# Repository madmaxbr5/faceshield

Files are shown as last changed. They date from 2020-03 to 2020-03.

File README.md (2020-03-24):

# faceshield
Plans and instructions for a laser-cut face shield for COVID-19 PPE.<br>
<a rel="Latest writeup is here" href="https://docs.google.com/document/d/1kkmi4AXXiO3MM34HUSQM1HEoQGzZ9lCmX02rIgVbk9Q/edit">Latest writeup is here</a>

<a rel= "Changelog" href="https://docs.google.com/spreadsheets/d/1W2J-ytu9fVvlhKfiAqHdhAEgvUPn8Wbc3KxeLBzUL18/edit#gid=0">Current Changlog is here.</a>

The intended material is .005"-.001" (5-10 mil) PET/Mylar/Duralar film or similar, and is available from craft stores or from plastic suppliers. A sourcing document is included in the files. 

Different materials may also be compatible but results are not guaranteed. It is unlikely that this design will be compatible with substrates greater than .015"; modifications will be studied for thicker substrates. 

This work is free to use and modify as needed for non-profit uses. Non-profit for the purpose of this license means revenues not to exceed recovery of material costs, distribution costs, and reasonable rates of manufacturing labor. This is to discourage profiteering or price gouging. Use for profiteering is strictly disallowed. 

<br />This work is licensed under a <a rel="license" href="http://creativecommons.org/licenses/by-sa/4.0/">Creative Commons Attribution-ShareAlike 4.0 International License</a>.

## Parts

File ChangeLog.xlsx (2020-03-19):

Version | Comments | Cut time | Assembly time | 40" Roll yield | Appx Cost per mask
2 | Initial released version | 0:47:00 | 1min | 192 | $0.26
9 | significant update to dimensions and tab structure | 0:45:00 | 2-3min | 225 | $0.22
12 | redesign and simplification of tabs. Tweak to dimensions. Substantial improvement in packing efficiency | 0:38:00 | 10sec | 252 | $0.20

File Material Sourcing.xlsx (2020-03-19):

Supplier | Item | Cost | Link
Grafix/Amazon | 40"x100ft .005 duralar | $98 | https://www.amazon.com/Grafix-Clear-Dura-Lar-40-Inch-100-Feet/dp/B0092MJLSO
Grafix direct | 40"x100ft .005 duralar | $50 (qty 25+) | ken@grafixplastics.com
US plastics | 40"x100ft .005 mylar | $117 | https://www.usplastic.com/catalog/item.aspx?itemid=36640&catid=748
petfilm.com | 1000ft roll .005 PET | TBD | under investigation
blick art | 40"x100ft .005 duralar | $135 | https://www.dickblick.com/items/55506-1509/
tap plastics | .005 mylar various sizes | varied but on the expensive side | https://www.tapplastics.com/product/plastics/plastic_sheets_rolls/mylar_rolls_clear/255

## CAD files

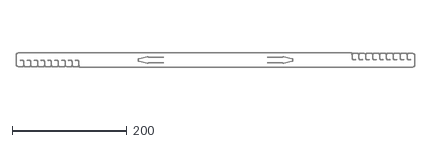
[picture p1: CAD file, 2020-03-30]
Origami_V20_Headband.dxf
694.9 x 25.9

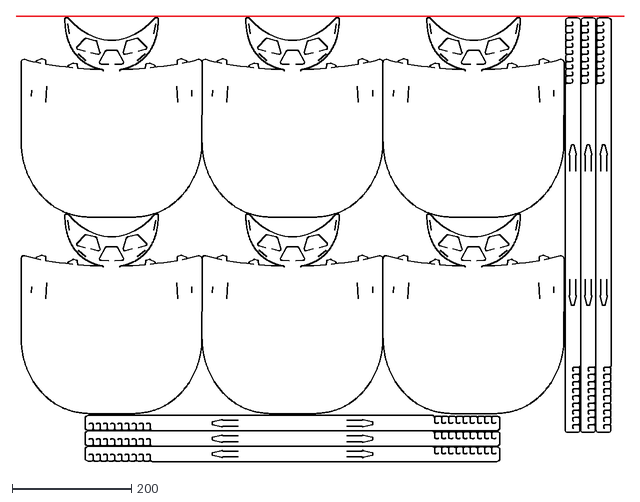
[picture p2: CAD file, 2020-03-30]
Origami_V20_40x30_array.dxf
1018.8 x 746.4

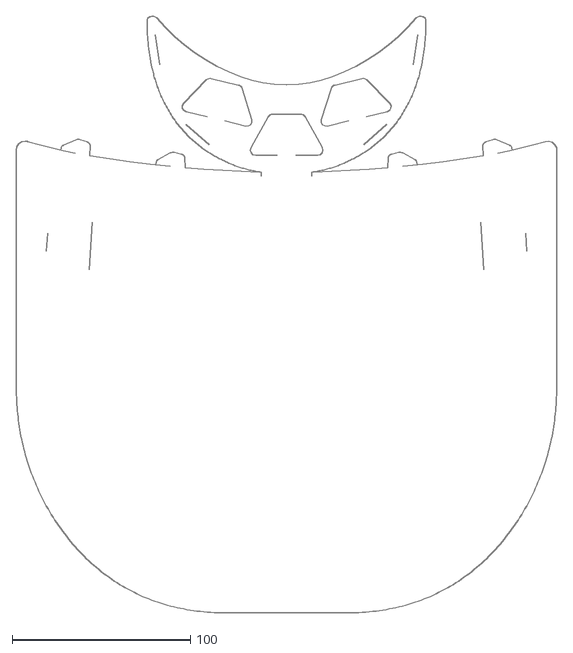
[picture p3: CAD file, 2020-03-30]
Origami_V20_Shield.dxf
303.2 x 334.5

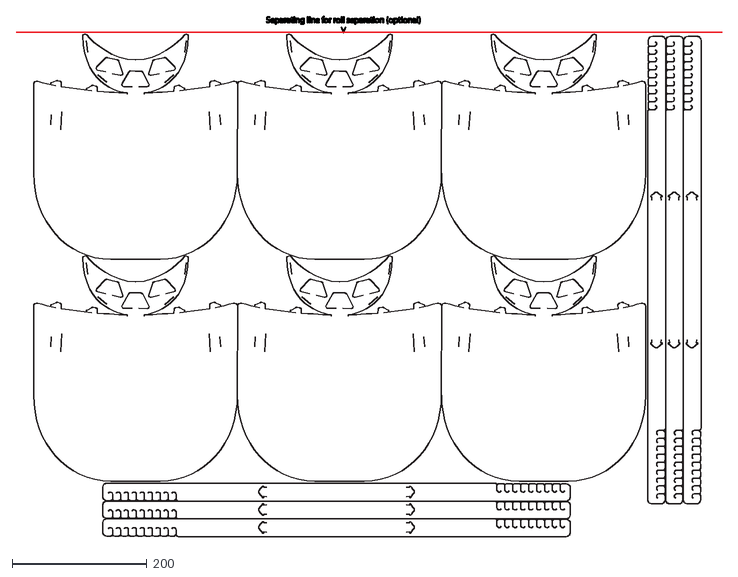
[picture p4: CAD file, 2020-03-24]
origami_face_shield_v16_40x30.dxf
1047.9 x 771.9

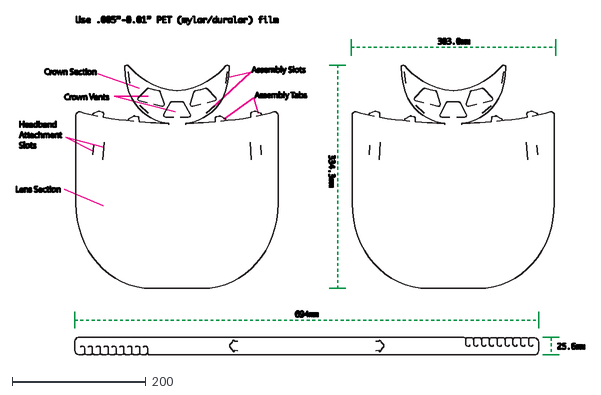
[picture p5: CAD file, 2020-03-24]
origami_face_shield_v16_master.dxf
851.1 x 507.3

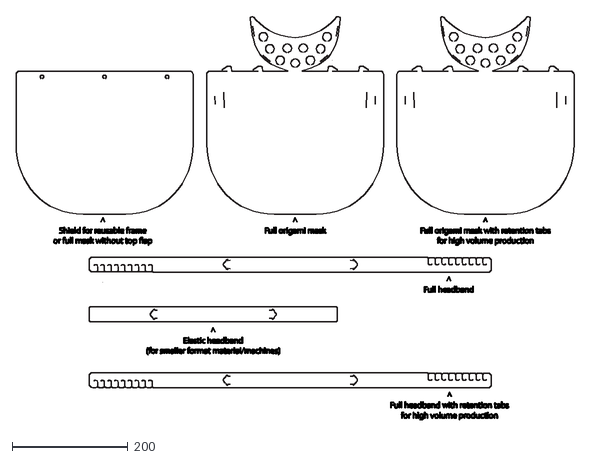
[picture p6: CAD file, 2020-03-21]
shield_laser_template_v15.dxf
962.5 x 696.4

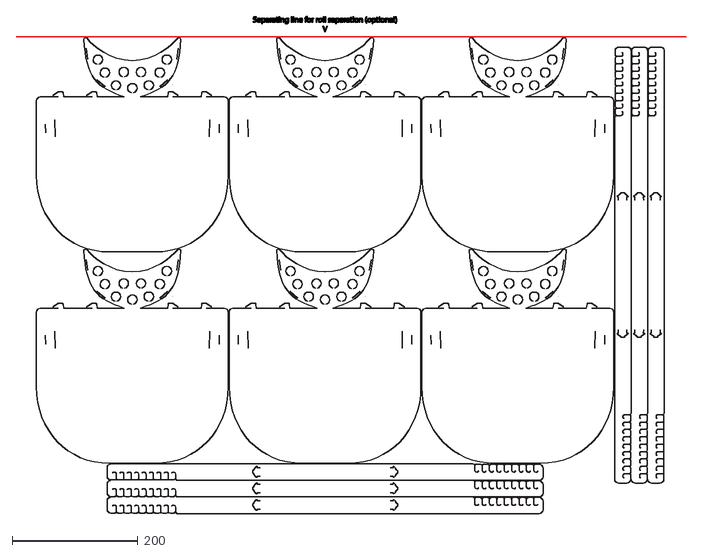
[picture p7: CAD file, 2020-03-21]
shield_laser_template_v15_40inch_roll.dxf
1066.8 x 791.4

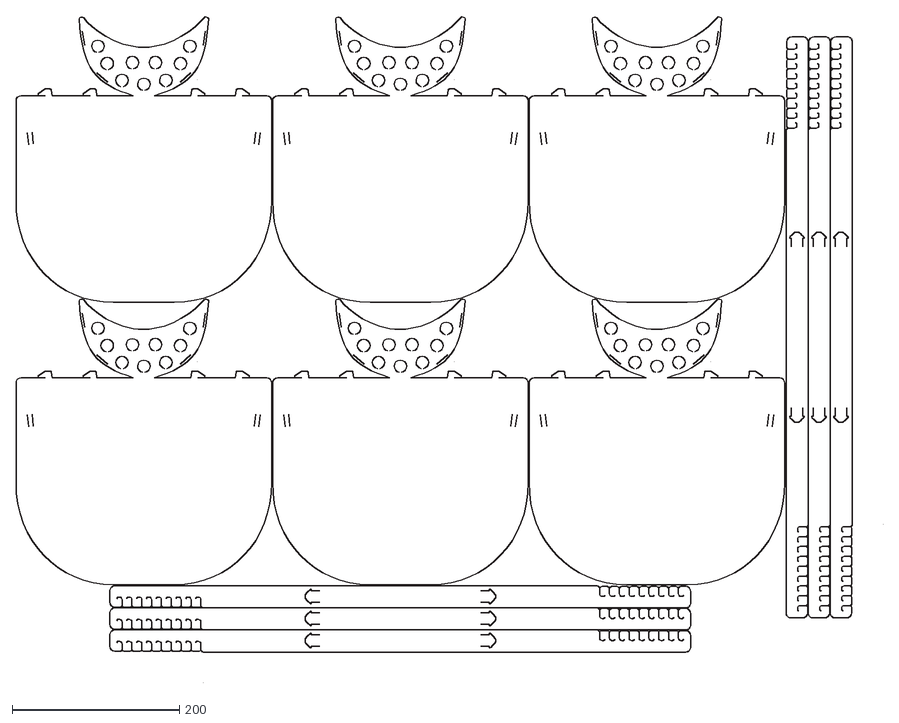
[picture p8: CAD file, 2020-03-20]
shield_laser_template_v14_40inch_roll_revised.dxf
1035.5 x 795.9

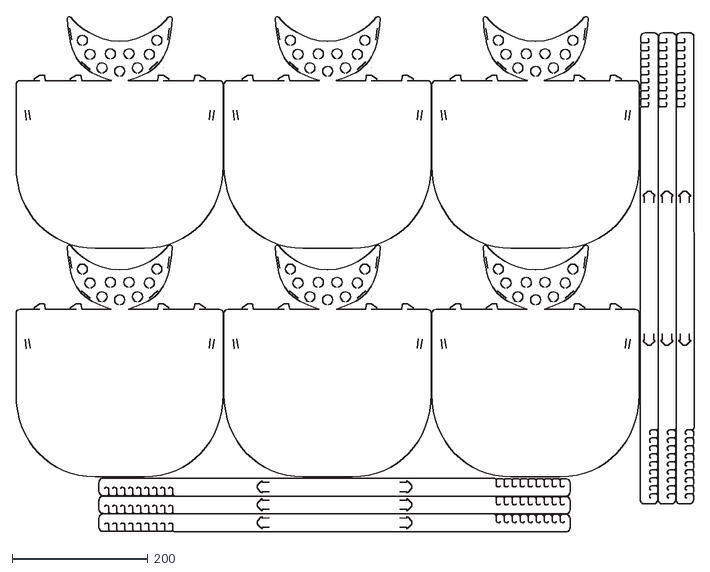
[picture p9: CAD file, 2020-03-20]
shield_laser_template_v14_40inch_roll.dxf
998.9 x 759.8

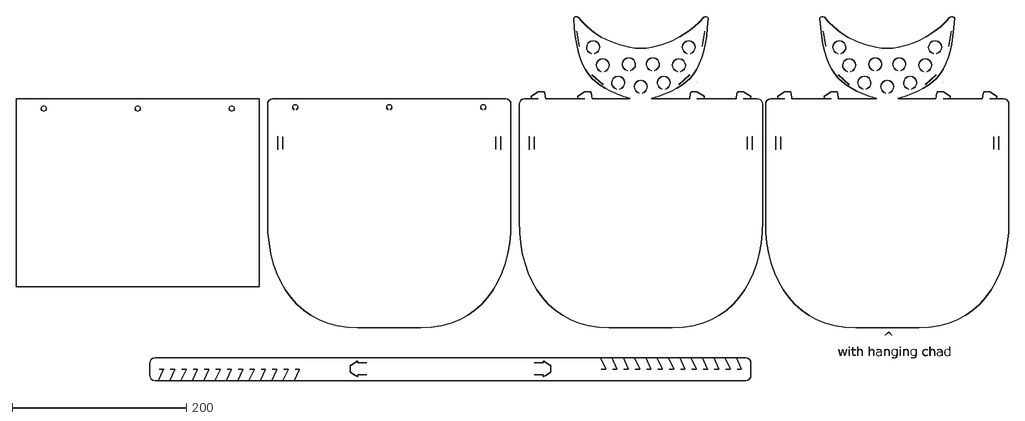
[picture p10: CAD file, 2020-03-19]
shield_laser_template_v12.dxf
^
with hanging chad

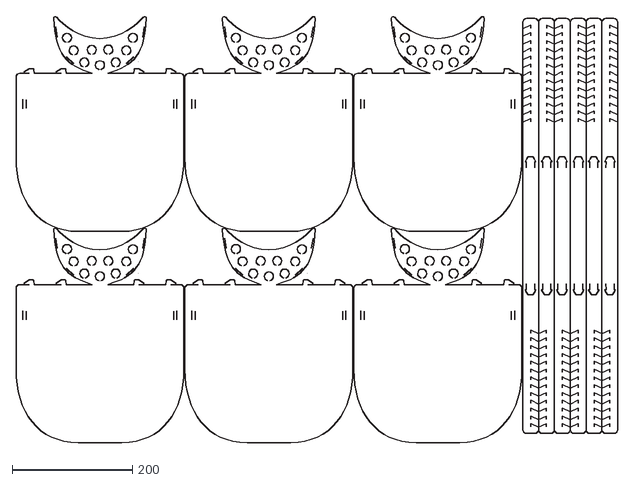
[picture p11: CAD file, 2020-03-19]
shield_laser_template_v12_bulk_40inch_roll.dxf
1001.3 x 709.1

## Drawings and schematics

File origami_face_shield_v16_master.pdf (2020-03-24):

## Use .005”-0.01” PET (mylar/duralar) film

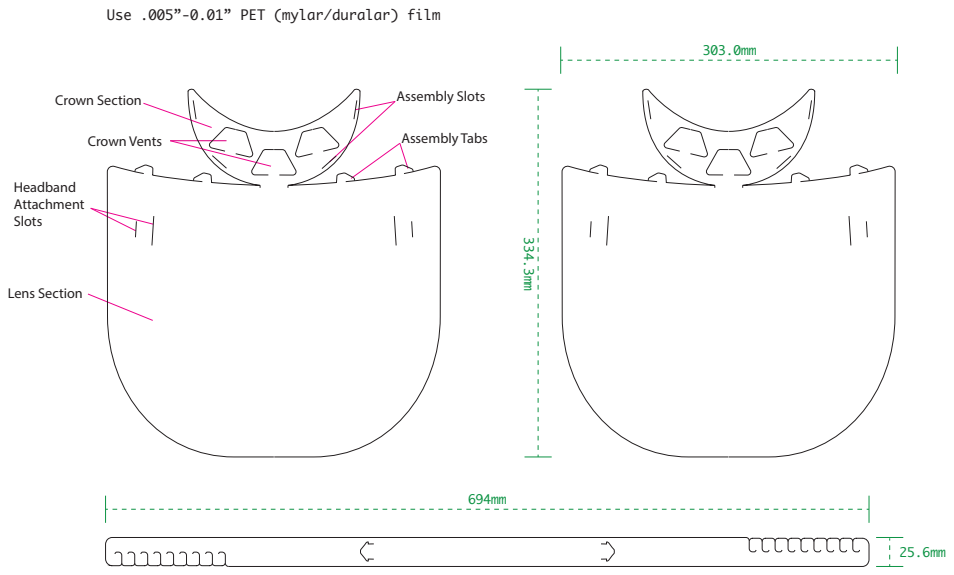
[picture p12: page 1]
Lens Section; Crown Section; Crown Vents; Headband Attachment Slots; Assembly Slots; Assembly Tabs

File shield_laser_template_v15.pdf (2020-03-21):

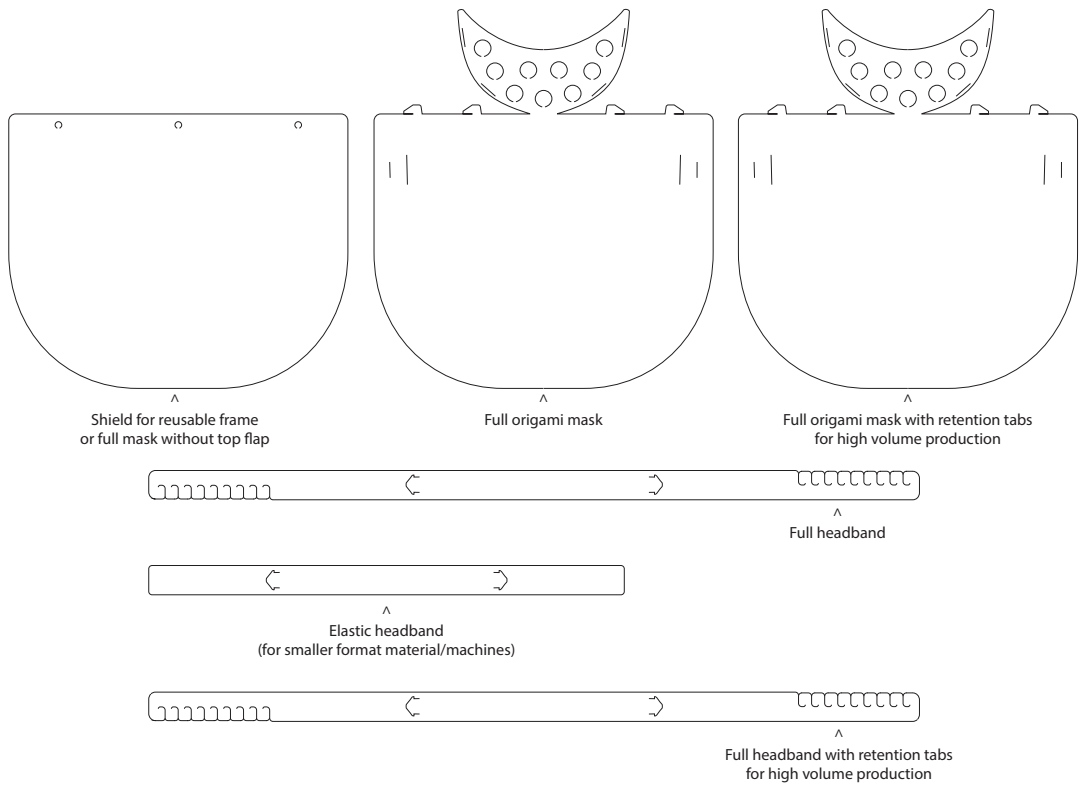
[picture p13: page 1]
^ Full headband; ^ Elastic headband

Full origami mask

Shield for reusable frame
or full mask without top ap

Full origami mask with retention tabs
for high volume production

(for smaller format material/machines)

Full headband with retention tabs

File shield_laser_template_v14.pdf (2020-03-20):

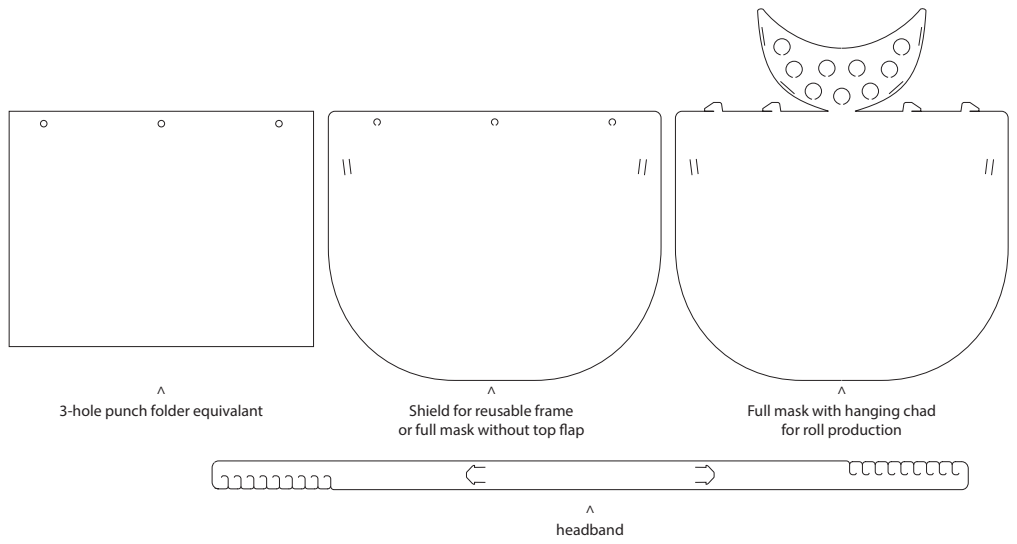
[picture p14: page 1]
^ headband

3-hole punch folder equivalant

Shield for reusable frame
or full mask without top ap

Full mask with hanging chad
for roll production

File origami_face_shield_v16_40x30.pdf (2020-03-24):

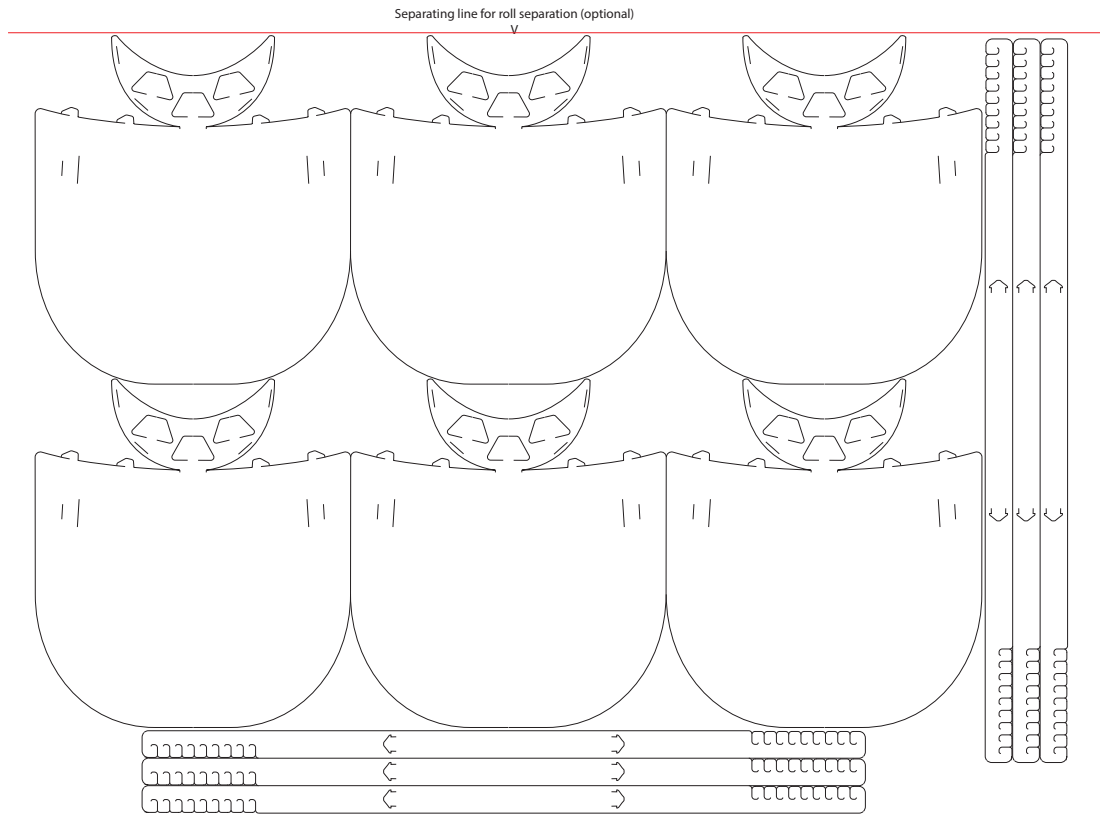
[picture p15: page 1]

Separating line for roll separation (optional)

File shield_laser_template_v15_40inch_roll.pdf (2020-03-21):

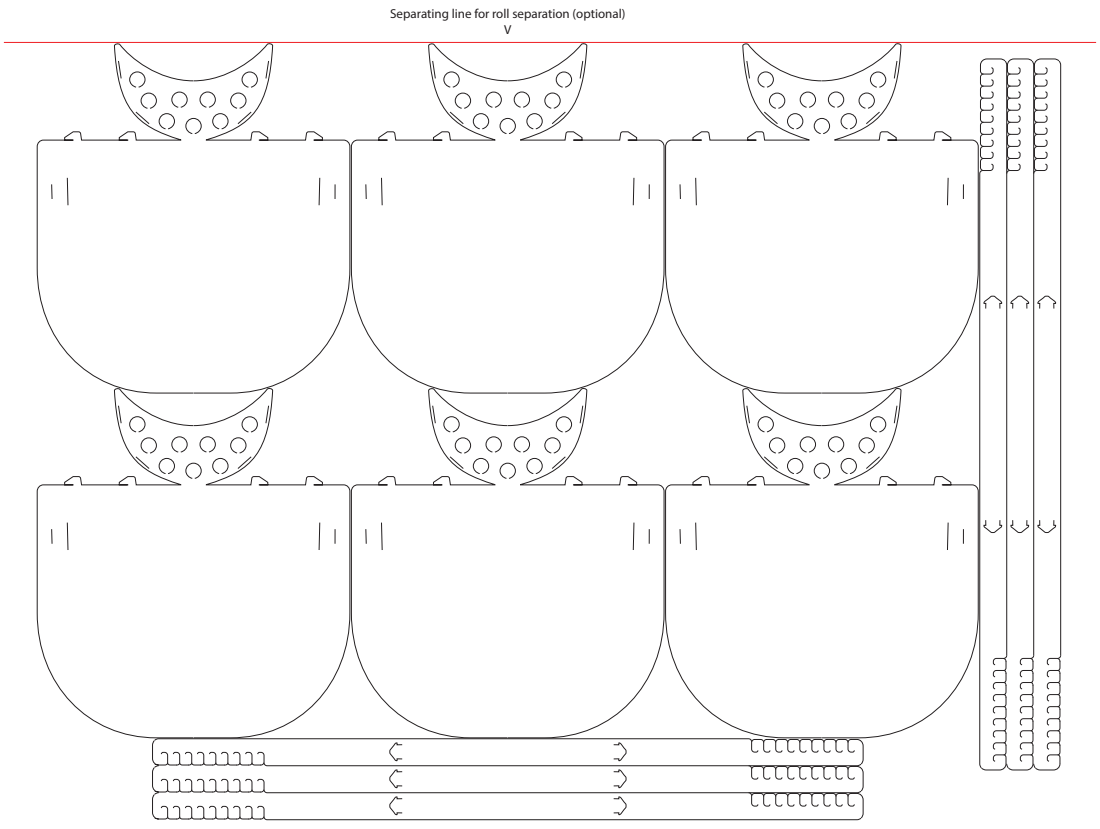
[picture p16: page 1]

Separating line for roll separation (optional)

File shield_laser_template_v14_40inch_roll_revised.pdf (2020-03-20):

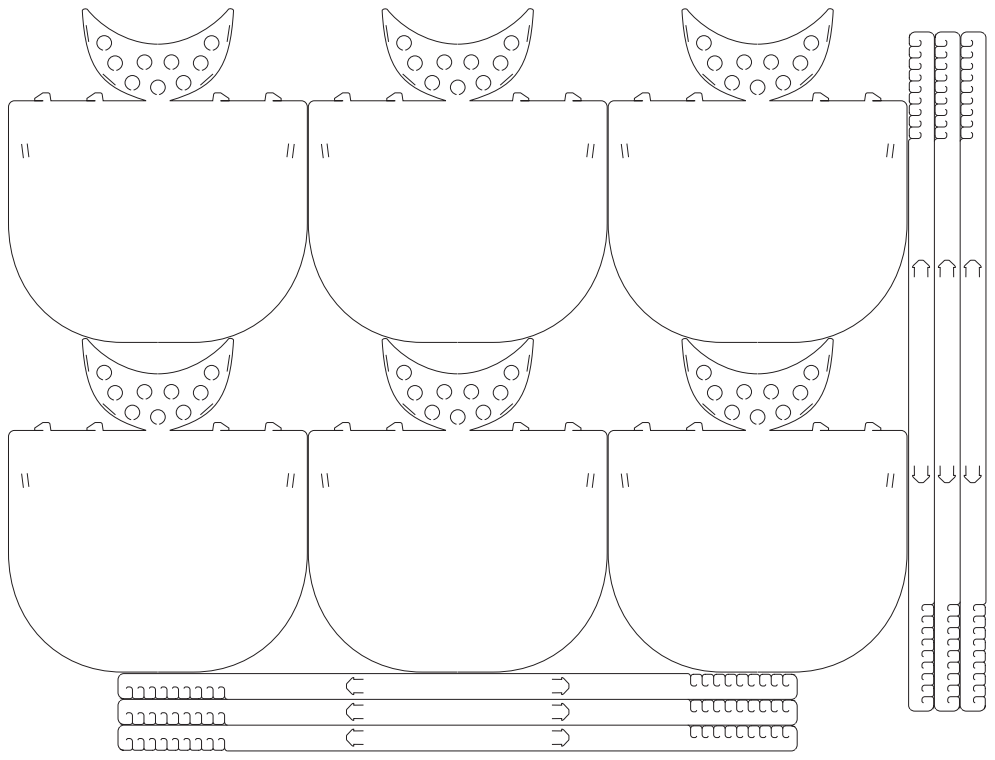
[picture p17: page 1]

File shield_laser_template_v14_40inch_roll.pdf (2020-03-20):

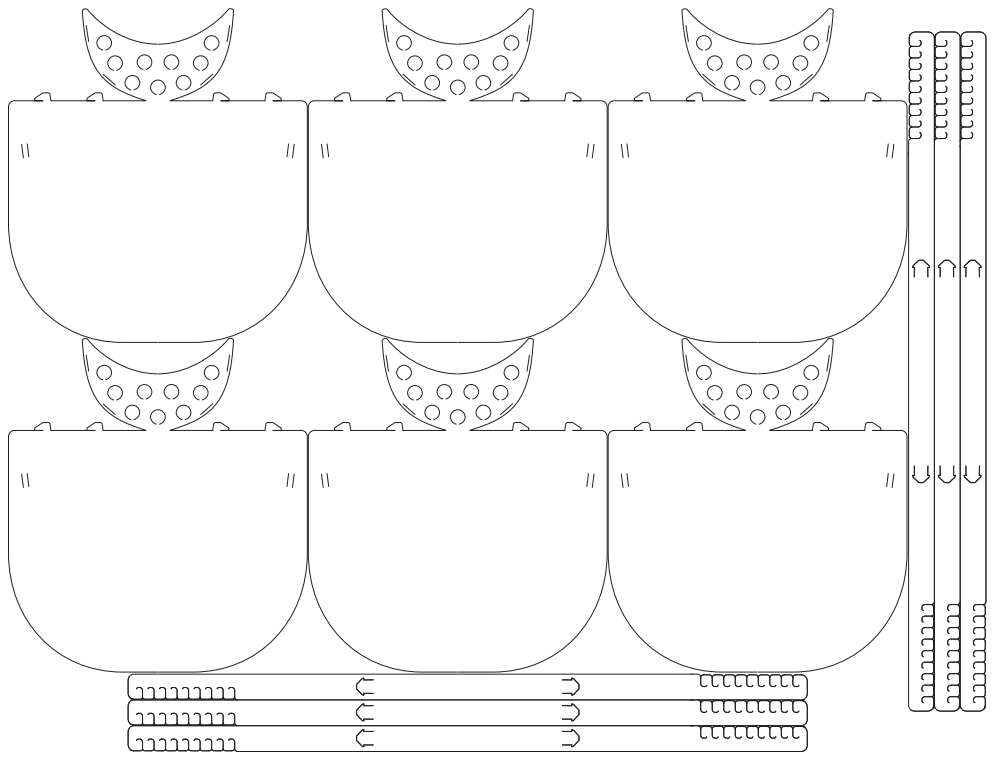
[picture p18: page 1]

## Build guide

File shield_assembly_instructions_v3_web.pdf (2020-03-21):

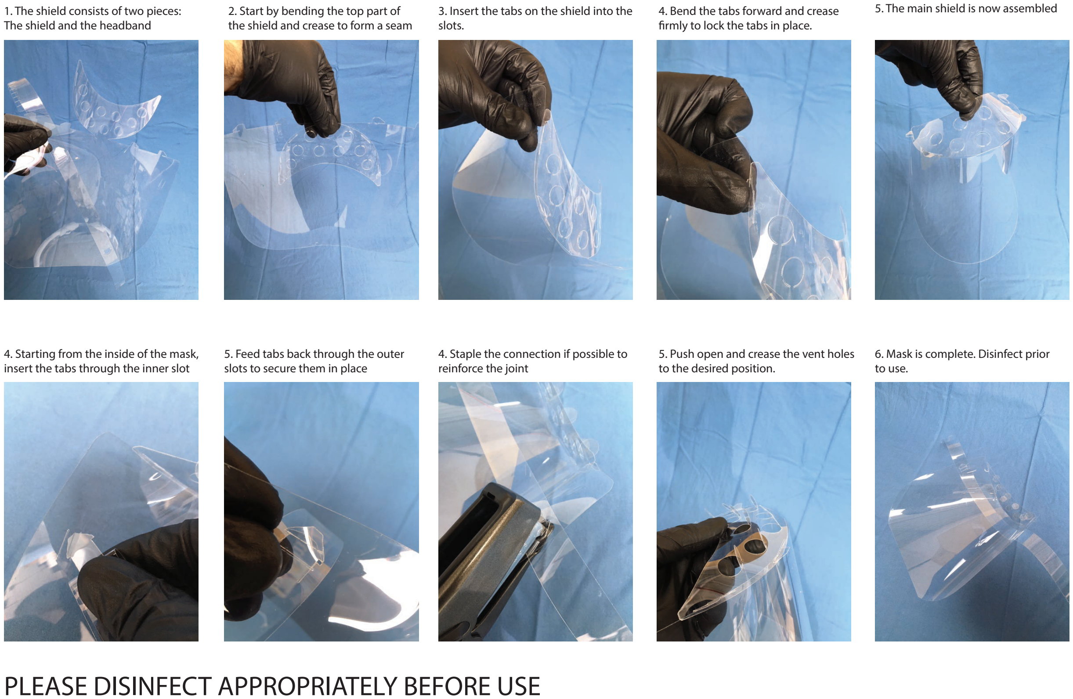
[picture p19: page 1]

1. The shield consists of two pieces: The shield and the headband
5. The main shield is now assembled
5. Push open and crease the vent holes to the desired position.

# PLEASE DISINFECT APPROPRIATELY BEFORE USE

2. Start by bending the top part of the shield and crease to form a seam
4. Bend the tabs forward and crease rmly to lock the tabs in place.
4. Starting from the inside of the mask, insert the tabs through the inner slot
3. Insert the tabs on the shield into the slots.
6. Mask is complete. Disinfect prior to use.
5. Feed tabs back through the outer slots to secure them in place
4. Staple the connection if possible to reinforce the joint

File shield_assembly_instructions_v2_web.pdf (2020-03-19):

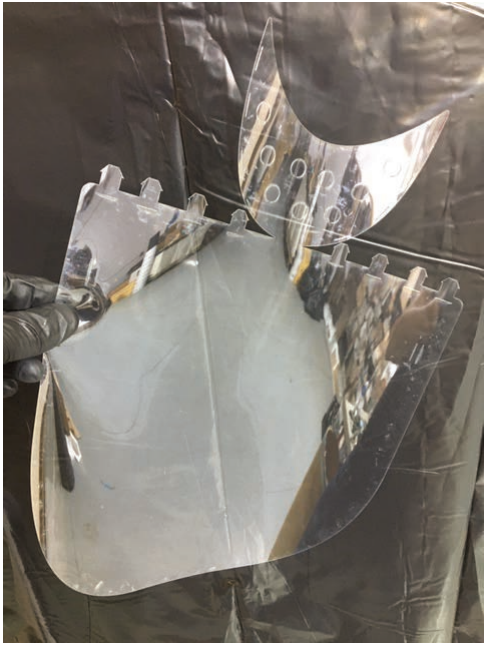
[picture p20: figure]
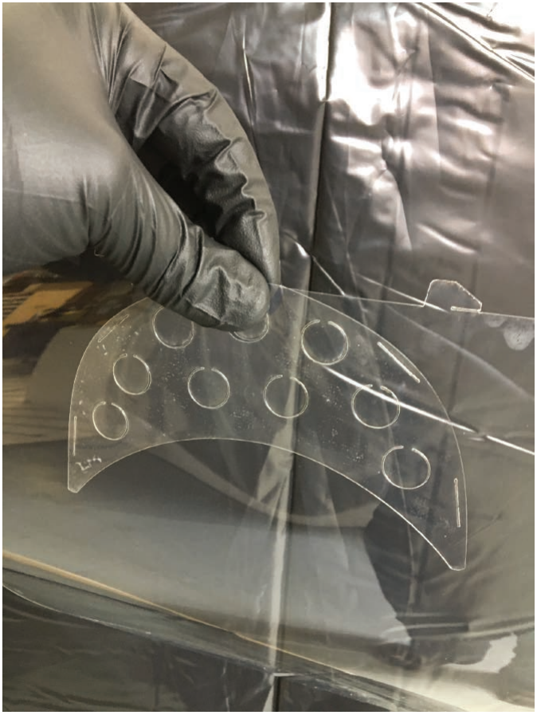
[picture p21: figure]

1. The sheild consists of two pieces:
- The primary shield

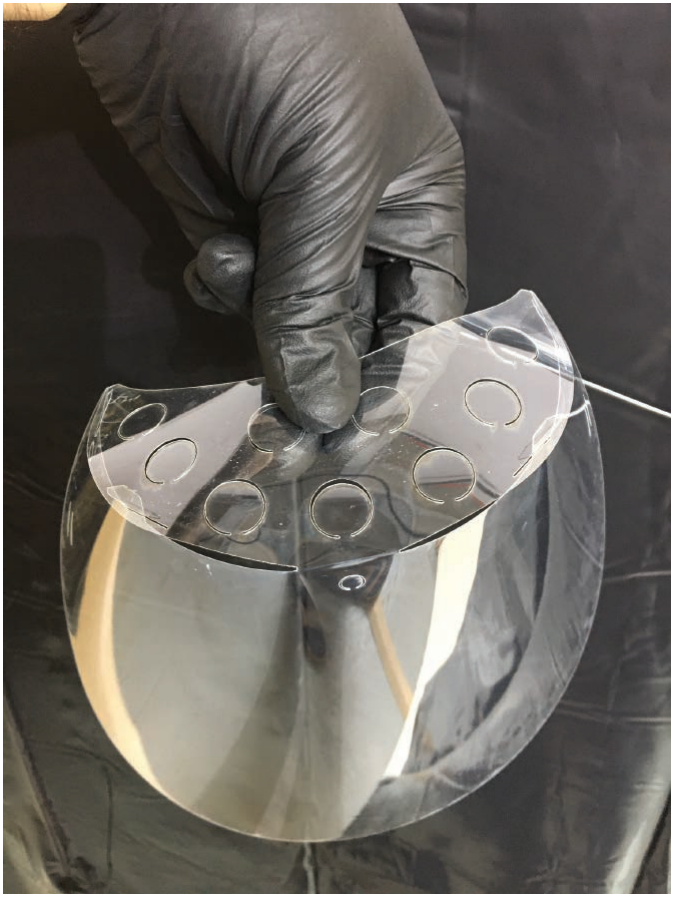
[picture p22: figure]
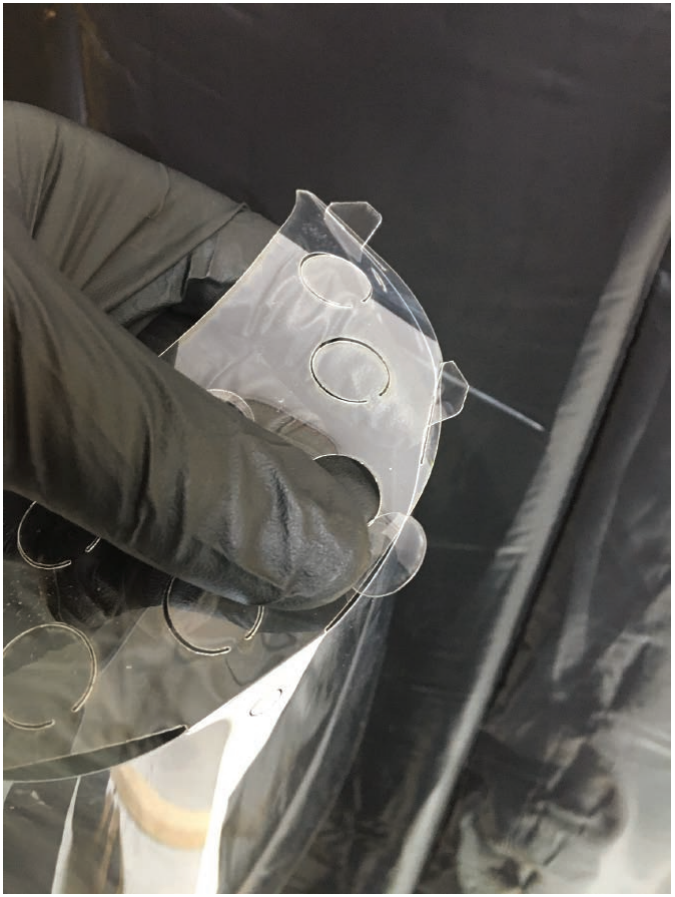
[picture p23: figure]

5. The main shield is now assembled 5. Push open and crease the vent holes to the desired position.

# PLEASE SANITIZE APPROPRIATELY BEFORE USE

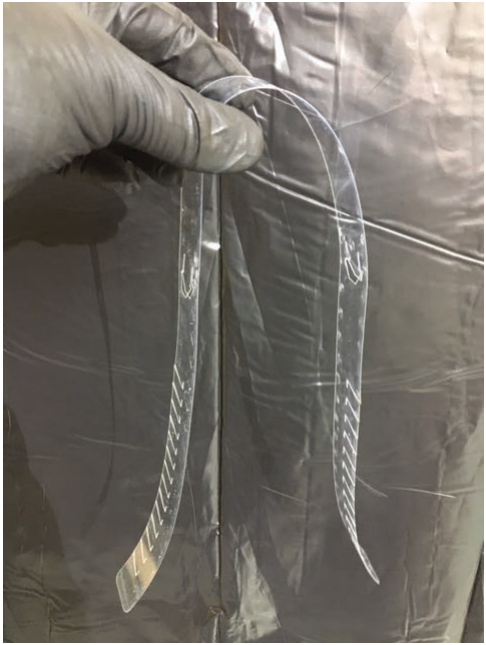
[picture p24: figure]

- And the headband | 2. Start by bending the top part of the shield and crease to form a seam

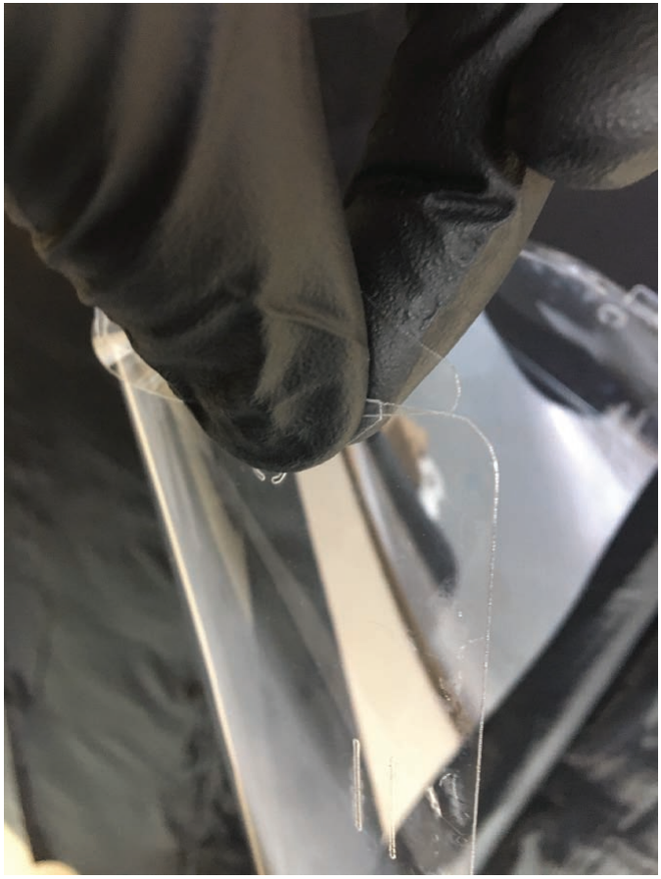
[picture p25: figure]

4. Bend the tabs forward and crease rmly to lock the tabs in place.

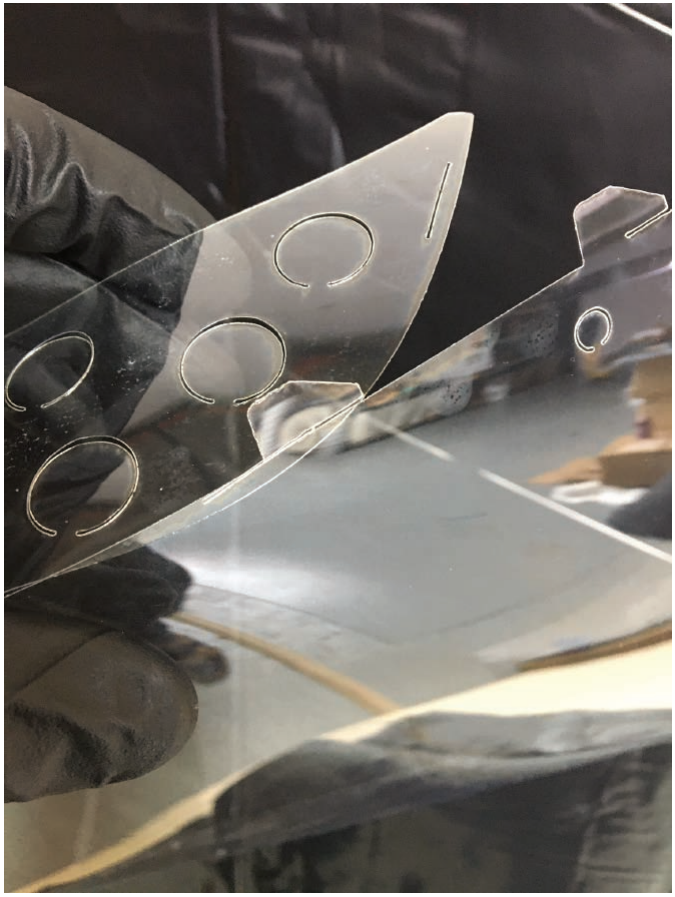
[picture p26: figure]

3. Insert the tabs on the shield into the slots.

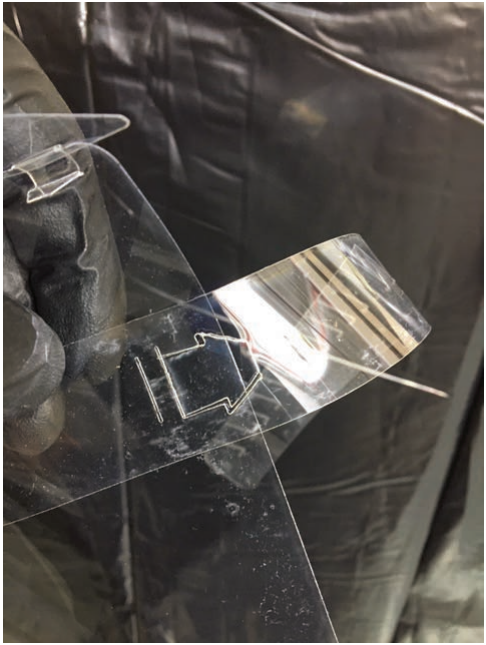
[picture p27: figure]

7. Push a tab of the headband through the outer slot on the side of the shield

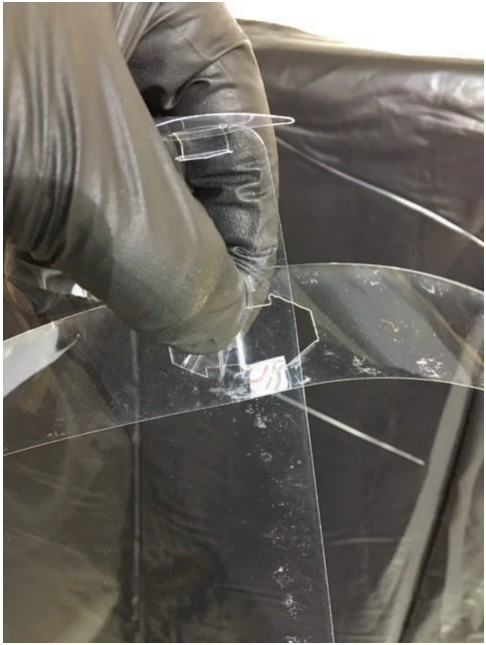
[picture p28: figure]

8. Bend the tab back toward the front of the shield and crease sharply

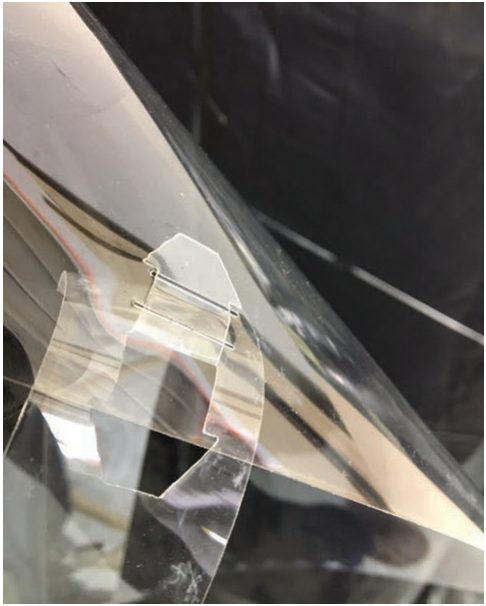
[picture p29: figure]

9. Insert the tab through the inner slot on the shield. (Alternatively, this connection can be stapled in place)

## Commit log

2020-03-24 Add files via upload
    V16 of the design
    [origami_face_shield_v16_master.dxf]
2020-03-30 Add files via upload
    V20 with updated headband attachment tabs for more intuitive assembly
    [Origami_V20_40x30_array.dxf, Origami_V20_Headband.dxf, Origami_V20_Shield.dxf]
